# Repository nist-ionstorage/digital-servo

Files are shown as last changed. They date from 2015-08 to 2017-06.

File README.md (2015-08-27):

# NIST Digital Servo

Ion Storage Group  
Time and Frequency Division  
National Institute of Standards and Technology  
Boulder, CO USA

Authors:  
David Leibrandt (david.leibrandt@nist.gov)  
Jason Heidecker

The NIST digital servo is designed to be a general purpose feedback controller, implemented digitally using an FPGA.  The advantages of an all-digital approach include fast and easy (no soldering) reconfiguration of the feedback transfer function, loop shapes that go beyond PID, the ability to perform automatic lock acquisition, and the integration of diagnostics for easy analysis of open and closed loop system performance.  The NIST digital servo has been optimized for feedback control of lasers in atomic, molecular, and optical (AMO) physics experiments, but it should be applicable in other control applications with similar bandwidth, noise, and loop shape requirements.

This github repository contains the hardware, firmware, and software design files, as well as precompiled firmware and software binaries to run the digital servo on Windows 7.

For more information about the firmware and performance of the digital servo, as well as example use cases, please refer to D. R. Leibrandt and J. Heidecker, [arXiv:1508.06319](http://arxiv.org/abs/1508.06319) (2015).

For instructions on setting up the digital servo using the precompiled binaries on Windows 7 (which does not require installing or using any compilers) and on operation of the GUI, please see `doc\NIST_digital_servo_manual.pdf`.

The hardware design and fabrication files are located in the `hardware` folder.  The firmware source code files are located in the `firmware` folder.  The GUI source code files are located in the `gui` folder.  And matlab functions for reading in data files generated by the digital servo are located in the `matlab` folder.

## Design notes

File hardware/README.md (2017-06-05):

# OK6010_DB

Ion Storage Group  
Time and Frequency Division  
National Institute of Standards and Technology  
Boulder, CO USA

Authors:  
Jason Heidecker  
David Leibrandt (david.leibrandt@nist.gov)

The OK6010_DB is a an open source hardware daughterboard to the Opal Kelly XEM6010-LX150 that provides two channels of 100 MSPS 16 bit ADC, two channels of 100 MSPS 16 bit DAC, and one channel of 1 MSPS 20 bit DAC.

This directory contains all of the Altium Designer schematic and board files.  A complete set of fabrication files can be found in the `Project Outputs for OK6010_DB` folder.  Design files for an enclosure can be found in the `Enclosure` folder.

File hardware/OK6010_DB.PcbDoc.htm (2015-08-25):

Reporting Options

# File in Previous Format

Date | : | 8/14/2015
Time | : | 2:22:02 PM
Filename | : | C:\dev\digital-servo\hardware\OK6010_DB\OK6010_DB.PcbDoc

Version | Warning
Release 12 | CAUTION - Air Gap Width previously controlled by Clearance rule is now controlled by Polygon Connect Style rule's newly introduced Air Gap Width (set to default value). Suggest reviewing each Polygon Connect Style rule's Air Gap Width attribute for correctness.
Release 13 | CAUTION - Silkscreen Over Component Pads Rules are converted to Silk To Solder Mask Clearance Rules. Suggest examining rule scopes for accuracy.

This file was generated by an earlier version of the software

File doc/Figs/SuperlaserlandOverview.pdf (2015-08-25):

Fast
analog
input
settings settings

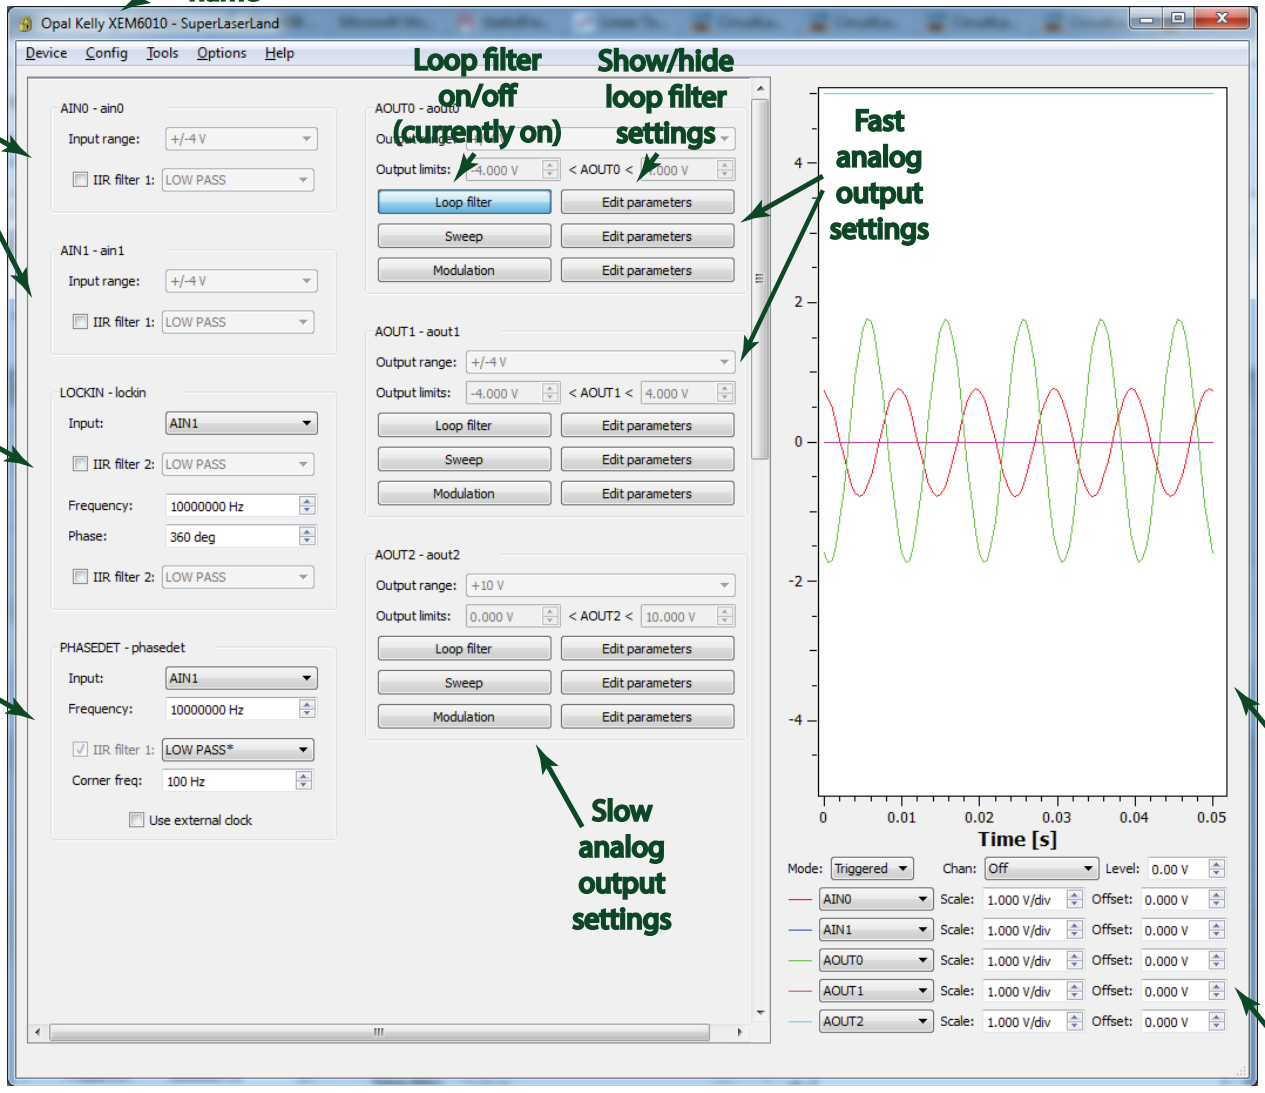
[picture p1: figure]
Fast analog output settings settings; Slow analog output settings settings; Loop filter Loop filter on/off (currently on) (currently on); Show/hide Show/hide loop filter loop filter settings settings

Lockin
amplifier amplifier
settings settings

Phase
detector detector
settings settings

Scope
settings settings

Scope
plot

Lock box Lock box
name

(b)

(a)

VGA setting VGA setting
Firmware output range limits Firmware output range limits

Loop filter input signal, offset, and sign Loop filter input signal, offset, and sign
Second order IIR filter (currently disabled) Second order IIR filter (currently disabled)

First order IIR filter First order IIR filter
(currently enabled and set to a PI loop shape) (currently enabled and set to a PI loop shape)

First order IIR filter First order IIR filter
(currently enabled and set to a PD loop shape) (currently enabled and set to a PD loop shape)

First order IIR filter (currently disabled) First order IIR filter (currently disabled)
Loop filter hold (currently disabled) Loop filter hold (currently disabled)
Loop filter hold falling and rising edge delay Loop filter hold falling and rising edge delay

Sweep center Sweep center
Sweep amplitude Sweep amplitude
Sweep frequency Sweep frequency

Amplitude of LOCKIN LO added to AOUT0 Amplitude of LOCKIN LO added to AOUT0

LOCKIN LO frequency LOCKIN LO frequency and phase and phase
LOCKIN post-filter LOCKIN post-filter

LOCKIN pre-filter LOCKIN pre-filter

LOCKIN input signal LOCKIN input signal

PHASEDET input signal PHASEDET input signal PHASEDET LO frequency PHASEDET LO frequency PHASEDET post-filter PHASEDET post-filter (currently set to a (currently set to a low-pass with a low-pass with a corner frequency corner frequency of 100 Hz.) of 100 Hz.)

AIN0 post-filter AIN0 post-filter (currently disabled) (currently disabled)

AOUT0 settings: AOUT0 settings: AIN0 VGA setting AIN0 VGA setting

Loop filter automatic relock (currently disabled) Loop filter automatic relock (currently disabled)

Loop filter clear when railed (currently disabled) Loop filter clear when railed (currently disabled)

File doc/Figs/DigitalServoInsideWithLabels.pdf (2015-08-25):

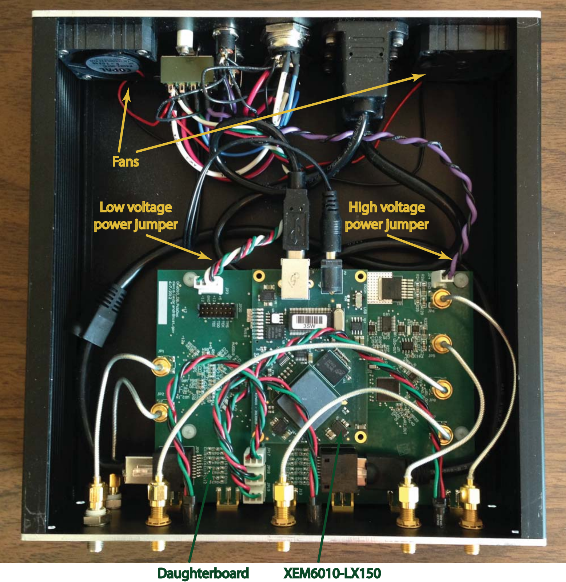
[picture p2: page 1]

Fans

Low voltage Low voltage
power jumper power jumper

High voltage High voltage
power jumper power jumper

Daughterboard Daughterboard XEM6010-LX150 XEM6010-LX150

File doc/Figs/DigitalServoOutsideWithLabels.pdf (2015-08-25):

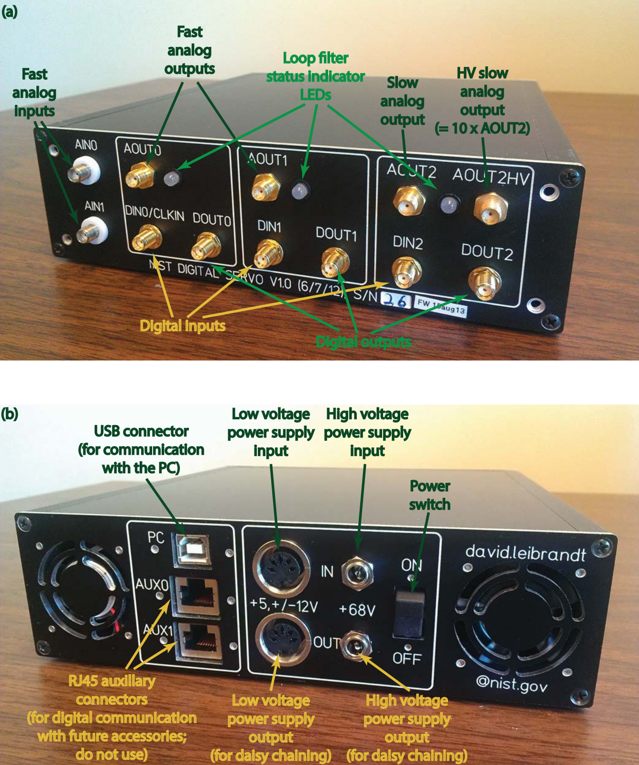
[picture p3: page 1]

Low voltage Low voltage
power supply power supply
input

High voltage High voltage
power supply power supply
input

Low voltage Low voltage
power supply power supply
output
(for daisy chaining) (for daisy chaining)

High voltage High voltage
power supply power supply
output
(for daisy chaining) (for daisy chaining)

Power
switch

USB connector USB connector (for communication (for communication with the PC) with the PC)

RJ45 auxillary RJ45 auxillary
connectors connectors
(for digital communication (for digital communication with future accessories; with future accessories; do not use) do not use)

(b)

(a)

Fast
analog
inputs

Fast
analog
outputs outputs
Slow
analog
output

HV slow HV slow
analog
output
(= 10 x AOUT2) (= 10 x AOUT2)

Digital inputs Digital inputs Digital outputs Digital outputs

Loop filter Loop filter
status indicator status indicator LEDs

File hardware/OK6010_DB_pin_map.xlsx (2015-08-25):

XEM6010 |  |  | FPGA |  |  |  | Daughterboard |  | Total |  | Differential | Mean |  | Notes
Jumper | Pin | Length [mm] | Bank | Description | Pin number | BUFIO2 Region | Description | Length [mm] | Length [mm] | Delay [ns] | Length [mm] | Delay [ns]
2 | 16 | 38.591 | 1 | L74P_1 | T19 | RB | AD5791_SCS |  |  |  |  |  |  | Each BUFIO2 region has
2 | 18 | 40.628 | 1 | L74N_1 | T20 | RB | AD5791_SCK |  |  |  |  |  |  |  | 4 BUFIO2s
2 | 20 | 39.602 | 1 | L72P_1 | P17 | RB | AD5791_SDI
2 | 22 | 33.852 | 1 | L72N_1 | N16 | RB | AD5791_SDO |  |  |  |  |  |  | Each bank has
2 | 28 | 36.711 | 1 | L73P_1 | P18 | RB | AD5791_LDAC |  |  |  |  |  |  |  | 2 BUFPLLs
2 | 26 | 34.914 | 1 | L71N_1 | M18 | RB | AD5791_CLR
2 | 24 | 34.813 | 1 | L71P_1 | M17 | RB | AD5791_RST |  |  |  |  |  |  | The XC6SLX45 has
 |  |  |  |  |  |  |  |  |  |  |  |  |  |  | 8 DCMs
1 | 17 | 35.889 | 1 | L9N_1 | G17 | RT | AD8251_IN_A0 |  |  |  |  |  |  |  | 4 PLLs
1 | 15 | 36.709 | 1 | L9P_1 | G16 | RT | AD8251_IN_A1 |  |  |  |  |  |  |  | 16 BUFGs
1 | 19 | 39.405 | 1 | L34P_1 | H19 | RT | AD8251_IN_WR0
1 | 21 | 36.649 | 1 | L34N_1 | H18 | RT | AD8251_IN_WR1 |  |  |  |  |  |  | Each IO tile can connect to
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

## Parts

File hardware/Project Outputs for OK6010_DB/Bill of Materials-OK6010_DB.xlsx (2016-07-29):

Designator | Comment | Footprint | Description | Quantity | Supplier 1 | Supplier Part Number 1 | Manufacturer 1 | Manufacturer Part Number 1
C1, C2, C9, C10, C40, C43 | 300pF | 0603w | capacitor | 6 | Digi-Key | 490-1438-1-ND | Murata Electronics North America | GRM1885C1H301JA01D
C3, C4, C8, C11, C14, C16, C17, C19, C22, C23, C28, C33, C34, C35, C39, C41, C42, C44, C45, C48, C50, C51, C54, C55, C58, C60, C62, C64, C65, C67, C68, C70, C72, C73, C76, C77, C78, C79, C80, C83, C85, C86, C87, C88, C89, C90, C91, C92, C94, C95, C96, C97, C99, C102, C103, C105, C106, C127 | 0.1uF | 0603w | capacitor | 58 | Digi-Key | 399-1281-1-ND | Kemet | C0603C104K3RACTU
C5, C7, C37, C38 | 0.1uF | 1206 | capacitor | 4 | Digi-Key | 490-1767-1-ND | Murata Electronics North America | GRM31C5C1E104JA01L
C6 | 2.2uF | 0805 CLL | INTERDIGITATED capacitor | 1 | Digi-Key | 445-3406-1-ND | TDK Corporation | CLLE1AX7S0G225M/0.95
C12 | 2.2uF | 0603w | capacitor | 1 | Digi-Key | 478-5316-1-ND | AVX Corporation | 06036C225KAT2A
C13, C15, C18, C20, C21, C30, C31, C32, C49, C52, C56, C59, C61, C63, C66, C69, C71, C74, C84, C98, C100, C104 | 10uF | 1206 | ELECTROLYTIC capacitor | 22 | Digi-Key | 493-4304-1-ND | Nichicon | F971C106MAA
C24, C29 | 33nF | 0805 | capacitor | 2 | Digi-Key | 490-3323-1-ND | Murata Electronics North America | GRM21BR72A333KA01L
C25 | 10pF | 0603w | capacitor | 1 | Digi-Key | 490-1403-1-ND | Murata Electronics North America | GRM1885C1H100JA01D
C26 | 10uF | 7243 V Type HD | ELECTROLYTIC capacitor | 1 | Digi-Key | PCE4986CT-ND | Panasonic Electronic Components | EEE-HD2A100P
C27 | 0.1uF | 0805 | capacitor | 1 | Digi-Key | 490-4789-1-ND | Murata Electronics North America | GCM21BR72A104KA37L
C36, C81, C82 | 1nF | 0603w | capacitor | 3 | Digi-Key | 490-1494-1-ND | Murata Electronics North America | GRM188R71H102KA01D
C46, C93 | 10uF | 0603w | capacitor | 2 | Digi-Key | 490-3896-1-ND | Murata Electronics North America | GRM188R60J106ME47D
C47, C53, C57, C75, C101 | 100uF | 1206 | capacitor | 5 | Digi-Key | 445-6008-1-ND | TDK Corporation | C3216X5R0J107M160AB
C107, C108, C109, C110 | 1.8pF | 0603w | capacitor | 4 | Digi-Key | 712-1328-1-ND | Johanson Technology Inc. | 251R14S1R8BV4T
C111, C112, C113, C114, C115, C116, C117, C118, C119, C120, C121, C122, C123, C124, C125, C126 | NOT STUFFED | 0603w | capacitor | 16
J11, J12, J13, J14, J15, J16 | SMA_EDGE | sma_edge | sma edge connector | 6 | Digi-Key | ACX1426-ND | Amphenol-RF Division | 132289
JP1, JP2, JP5, JP6, JP7, JP8 | SMA | sma_pcb_200 | sma connector | 6 | Digi-Key | A97594-ND | TE Connectivity AMP Connectors | 5-1814832-1
JP2_B, JP3_B | BTE-040-01-F-D-A | BTE-040-01-F-D-A | Samtec Connector 0.8mm 80pin | 2 | Newark | 89M7080 | SAMTEC | BTE-040-01-F-D-A
JP3 | SIP4 (PCB TERMINAL) | SIP4MOLEX | 4 pin molex connector | 1 | Digi-Key | WM2746-ND | Molex, LLC | 0022292041
JP4 | SIP2 (PCB TERMINAL) | SIP2MOLEX | 2 pin molex connector | 1 | Digi-Key | WM2744-ND | Molex, LLC | 0022292021
JP9, JP10 | RJ-45 | SMD_ETHERNET | ethernet connector | 2 | Digi-Key | RJSSE-5080-ND | Amphenol Commercial Products | RJSSE-5080
JP17, JP18, JP19 | SIP3 (PCB TERMINAL) | SIP3MOLEX | 3 pin molex connector | 3 | Digi-Key | WM2745-ND | Molex, LLC | 0022292031
JP20 | HEADER 7X2 | IDC14 SM 2MM | 14 pin 2mm IDC connector | 1 | Digi-Key | WM18641-ND | Molex, LLC | 0878321420
L1, L2, L7, L8, L9, L10, L11, L12, L15, L16, L25, L26, L27, L28 | 1.0uH | 1210 | inductor | 14 | Digi-Key | 490-2493-1-ND | Murata Electronics North America | LQH32CN1R0M23L
L3, L4, L5, L6, L13, L14, L17, L18, L19, L20, L21, L22, L23, L24 | 1.0uH | 0805 | inductor | 14 | Digi-Key | 490-4026-1-ND | Murata Electronics North America | LQM21FN1R0N00D
R1, R10, R11, R20 | 249* | 0603w | resistor | 4 | Digi-Key | RNCS0603BKE249RCT-ND | Stackpole Electronics Inc. | RNCS0603BKE249R
R2, R12 | 150* | 0603w | resistor | 2 | Digi-Key | RNCS0603BKE150RCT-ND | Stackpole Electronics Inc. | RNCS0603BKE150R
R3, R7, R13, R17 | 220* | 0603w | resistor | 4 | Digi-Key | RG16P220BCT-ND | Susumu | RG1608P-221-B-T5
R4, R6, R8, R14, R16, R18, R29, R30, R32, R33, R34, R36, R37, R38 | 49.9* | 0603w | resistor | 14 | Digi-Key | RNCS0603BKE49R9CT-ND | Stackpole Electronics Inc. | RNCS0603BKE49R9
R5, R15 | 100k | 0603w | resistor | 2 | Digi-Key | 311-100KHRCT-ND | Yageo | RC0603FR-07100KL
R9, R19 | 1M | 0603w | resistor | 2 | Digi-Key | 311-1.00MHRCT-ND | Yageo | RC0603FR-071ML
R21 | 1.5k | 0603w | resistor | 1 | Digi-Key | 311-1.50KHRCT-ND | Yageo | RC0603FR-071K5L
R22, R41 | 140k | 0603w | resistor | 2 | Digi-Key | 311-140KHRCT-ND | Yageo | RC0603FR-07140KL
R23, R26 | 49.9* | 1206 | resistor | 2 | Digi-Key | RG32P49.9BCT-ND | Susumu | RG3216P-49R9-B-T1
R24 | 9.1k * | 0805 | resistor | 1 | Digi-Key | RG20P9.1KBCT-ND | Susumu | RG2012P-912-B-T5
R25 | 1k * | 0805 | resistor | 1 | Digi-Key | RG20P1.0KBCT-ND | Susumu | RG2012P-102-B-T5
R27 | 1K | 0603w | resistor | 1 | Digi-Key | 311-1.00KHRCT-ND | Yageo | RC0603FR-071KL
R28 | 287 | 0603w | resistor | 1 | Digi-Key | 311-287HRCT-ND | Yageo | RC0603FR-07287RL
R31 | 10k* | 0603w | resistor | 1 | Digi-Key | RG16P10.0KBCT-ND | Susumu | RG1608P-103-B-T5
R35, R39, R62, R63, R64, R65, R66, R67, R68, R69 | 0 | 0603w | resistor | 10 | Digi-Key | P0.0GCT-ND | Panasonic Electronic Components | ERJ-3GEY0R00V
R40, R42 | 78.7k | 0603w | resistor | 2 | Digi-Key | 311-78.7KHRCT-ND | Yageo | RC0603FR-0778K7L
R43, R45 | 76.8k | 0603w | resistor | 2 | Digi-Key | 311-76.8KHRCT-ND | Yageo | RC0603FR-0776K8L
R44, R46 | 147k | 0603w | resistor | 2 | Digi-Key | 311-147KHRCT-ND | Yageo | RC0603FR-07147KL
R47 | 10k | VFCD1505 | resistor network | 1 | Digi-Key | Y1685-10K/10K-ND | Vishay Foil Resistors (Division of Vishay Precision Group) | Y1685V0001TT9W
R48 | 107k | 0603w | resistor | 1 | Digi-Key | 311-107KHRCT-ND | Yageo | RC0603FR-07107KL
R49 | 93.1K | 0603w | resistor | 1 | Digi-Key | 311-93.1KHRCT-ND | Yageo | RC0603FR-0793K1L
R50, R51, R52, R53 | 2k | 0603w | resistor | 4 | Digi-Key | 311-2.00KHRCT-ND | Yageo | RC0603FR-072KL
R54, R55, R56, R57 | 75* | 0603w | resistor | 4 | Digi-Key | RNCS0603BKE75R0CT-ND | Stackpole Electronics Inc. | RNCS0603BKE75R0
R58, R59, R60, R61, R70, R71 | 62 | 0603w | resistor | 6 | Digi-Key | 541-62.0HCT-ND | Vishay Dale | CRCW060362R0FKEA
U1 | LTC2195 | UKG - QFN52 | 16 bit, low power, dual ADC | 1 | Digi-Key | LTC2195CUKG#PBF-ND | Linear Technology | LTC2195CUKG#PBF
U2, U4, U13, U14 | AD8251 | MSOP10sm | Programmable Gain Instumentation Amp, IC AMP INST ICMOS LDRIFT 10MSOP, IC AMP INST ICMOS LDRIFT 10MSOP, IC AMP INST ICMOS LDRIFT 10MSOP | 4 | Digi-Key | AD8251ARMZ-ND | Analog Devices Inc. | AD8251ARMZ
U3, U5 | LTC6406 | MSOP08 | Differential ADC Driver | 2 | Digi-Key | LTC6406CMS8E#PBF-ND | Linear Technology | LTC6406CMS8E#PBF
U6 | ADR127 | TSOT-6 | Voltage Reference | 1 | Digi-Key | ADR127AUJZ-REEL7CT-ND | Analog Devices Inc. | ADR127AUJZ-REEL7
U7 | ADR445B | SOIC08 | Ultra Precision Low Noise XFET Voltage Reference | 1 | Digi-Key | ADR445BRZ-ND | Analog Devices Inc. | ADR445BRZ
U8 | AD8676 | MSOP08 | ultraprecision dual rail-to-rail op amp | 1 | Digi-Key | AD8676BRMZ-REELCT-ND | Analog Devices Inc. | AD8676BRMZ-REEL
U9, U19 | AD8675 | MSOP08 | ultraprecision rail-to-rail op amp | 2 | Digi-Key | AD8675ARMZ-REELCT-ND | Analog Devices Inc. | AD8675ARMZ-REEL
U10 | AD5791 | TSSOP20 | DAC 20BIT SRL 20TSSOP | 1 | Digi-Key | AD5791ARUZ-ND | Analog Devices Inc. | AD5791ARUZ
U11 | OPA453 | DDPAK-7 | 80 V op amp | 1 | Mouser | 595-OPA453FAKTWT | Loading... | Loading...
U12 | AD9783 | LFCSP72 | DAC LVDS DUAL16BIT 500MSPS | 1 | Digi-Key | AD9783BCPZ-ND | Analog Devices Inc. | AD9783BCPZ
U15, U16, U17, U18, U20 | ADP3336 | MSOP08 | regulator | 5 | Digi-Key | ADP3336ARMZ-REEL7CT-ND | Analog Devices Inc. | ADP3336ARMZ-REEL7

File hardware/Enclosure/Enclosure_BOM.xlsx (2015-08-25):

Description | Quantity | Supplier | Supplier part #
Power supply +5V, +/-12V | 1 | Newark | 28M9050
Bulkhead 5 pin DIN | 2 | Digikey | CP-1235-ND
Power jumper cable, 1 ft | 0 | Amazon | http://www.amazon.com/Hosa-MID301BK-Standard-Cable-Black/dp/B000068NTK/ref=zg_bs_11973431_11
Power supply connector | 0 | Newark | SP119M-5P
56 V power supply | 1 | Digikey | 993-1023-ND
Bulkhead 2.1mm jack | 2 | Digikey | CP-5-ND
HV power jumper cable, 1 ft | 0 | Amazon | http://www.amazon.com/Male-2-1mm-Plug-Power-Adapter/dp/B0048O2XXG/ref=pd_sim_sbs_p_7
4PDT rocker switch | 1 | Digikey | 360-2276-ND
0.25" 2-56 standoff | 2 | Digikey | 492-1059-ND
2-56 x 3/8" socket cap screw | 2 | Mcmaster | 92196A079
Ethernet bulkhead female to male | 2 | Frontx | P115, 12 inch
USB bulkhead female to male | 1 | Frontx | P112, 6 inch
4-40 x 1/4" socket cap screw | 6 | Mcmaster | 92196A106
Fan | 2 | Digikey | 563-1130-ND
4-40 x 3/8" socket cap screw | 8 | Mcmaster | 92196A108
Bulkhead SMA female to SMA female, isolated ground | 2 | Pasternack | PE9067
Bulkhead SMA female to SMA female | 4 | Digikey | ARF1207-ND
Two color LED | 3 | Digikey | 350-2131-ND
0.438" 4-40 plastic standoff | 4 | Digikey | 492-1092-ND
4-40 plastic washer | 4 | Digikey | 3348K-ND
0.625" 4-40 plastic screw | 4 | Digikey | H548-ND
XEM6010 power connector | 1 | Digikey | CP-2185-ND
Enclosure front panel | 1 | Front panel express | front.fpd
Enclosure back panel | 1 | Front panel express | back.fpd
Enclosure top panel | 1 | Front panel express | top.fpd
Enclosure bottom panel | 1 | Front panel express | bottom.fpd
Enclosure side panel | 2 | Front panel express | GL GP 10 23 - 200
Enclosure assembly kit (screws and feet) | 1 | Front panel express | GG MS 1123
Rack mount panel | 0.5 | Front panel express | rack mount panel.fpd
2 pin molex connector | 1 | Digikey | WM2613-ND
3 pin molex connector | 3 | Digikey | WM2626-ND
4 pin molex connector | 1 | Digikey | WM2614-ND
Molex connector terminals | 15 | Digikey | WM2624-ND
4" SMA cable | 3 | Digikey | ACX1664-ND
5" SMA cable | 2 | Digikey | ACX1665-ND
7" SMA cable | 1 | Digikey | ACX1667-ND
FPGA heat sink | 1 | Newark | 46T6813
FPGA integration PCB | 1 | Opal Kelly | XEM6010-LX150
Custom daughterboard PCB | 1 | Any | OK6010_DB

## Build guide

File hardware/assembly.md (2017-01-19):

Assembly instructions for the digital-servo box. 

## enclosure continutity
For safety reasons all sides of enclosure must be shorted to GND on power supply cable. 

## grounding of enclosure electrical connectors
All connector shields are shorted to enclosure except JP1 and JP2 which use isolated SMA.

## LED wiring
JP18, JP18, JP19 are labeled with GRN, GND, RED which corresponds to
the wire colors of the specified LEDs.

## AUX connector wiring 
AUX0 and AUX1 are used for expansion options. 
- AUX0 is routed to JP9. 
- AUX1 is routed to JP10.

## power connectors
Refer to the photo [here](https://github.com/nist-ionstorage/digital-servo/blob/master/doc/Figs/DigitalServoOutsideWithLabels.pdf). 

- For "Low voltage power supply input" and "Low voltage power supply
output" match wiring on connector from power supply brick 
(AEH45UM31 or [PCM50UT04](http://datasheet.octopart.com/PCM50UT04-XP-Power-datasheet-3173.pdf)).

- +5, -12, +12, GNDs from "Low voltage power supply input" are
permanently shorted to +5, -12, +12, GNDs on "Low voltage power supply
output".

- +68V on "High goltage power supply input" is permanently shorted to
"High voltage power supply output".

## power switch
Power Switch connects/disconnects -12, +12, +5, +68 to JP3, JP4 and the fans.

## wire color choice
If practical duplicate the wire color choice as in 
[this](https://github.com/nist-ionstorage/digital-servo/blob/master/doc/Figs/DigitalServoInsideWithLabels.pdf) photo. 

## wire gauge
Current for all power supplies is <= 5.0 A. Based on [this]
(http://assets.bluesea.com/files/resources/newsletter/images/DC_wire_selection_chartlg.jpg)
chart <= 16 AWG is sufficient. Use multi-strand wires throughout the
design (no mono-filament).

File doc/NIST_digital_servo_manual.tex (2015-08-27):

\documentclass[aip,rsi,preprint,graphicx]{revtex4-1}
\usepackage{graphicx}  % needed for figures
\usepackage{dcolumn}   % needed for some tables
\usepackage{bm}           % for math
\usepackage{amssymb} % for math
\usepackage{amsmath} % for math
\usepackage{hyperref} % for links

% avoids incorrect hyphenation
\hyphenation{FPGAs}

\begin{document}

\title{NIST digital servo manual}

\author{David~R.~Leibrandt}
\email{david.leibrandt@nist.gov}
\affiliation{National Institute of Standards and Technology\\325 Broadway St.~Boulder, CO 80305\\USA}

\date{\today}

\maketitle

\tableofcontents

%%%%%%%%%%%%%%%%%%%%%%%%%%%%%%%%%%%%%%%%%%%%%%%%%%
\section{Introduction}
%%%%%%%%%%%%%%%%%%%%%%%%%%%%%%%%%%%%%%%%%%%%%%%%%%

The NIST digital servo is designed to be a general purpose feedback controller, implemented digitally using an FPGA.  The advantages of an all-digital approach include fast and easy (no soldering) reconfiguration of the feedback transfer function, loop shapes that go beyond PID, the ability to perform automatic lock acquisition, and the integration of diagnostics for easy analysis of open and closed loop system performance.  The NIST digital servo has been optimized for feedback control of lasers in atomic, molecular, and optical (AMO) physics experiments, but it should be applicable in other control applications with similar bandwidth, noise, and loop shape requirements.  The key specifications (of hardware V1.0) are are:
\begin{itemize}
\item 1 FPGA (Xilinx Spartan 6 LX150)
\item 2 fast analog input channels (LTC2195, 16 bit, 100 MSPS, 50~nV$/\sqrt{\textrm{Hz}}$)
\item 2 fast analog output channels (AD9783, 16 bit, 100 MSPS, 40~nV$/\sqrt{\textrm{Hz}}$)
\item 1 slow analog output channel (AD5791, 20 bit, 1 MSPS, 20~nV$/\sqrt{\textrm{Hz}}$, optionally amplified to 0V to +65V output range for direct drive of PZTs)
\item Several digital I/O channels
\item 320 ns analog latency (ADC, digital signal processing, and DAC) including a digital PI filter
\item USB communication and GUI for setup and diagnostics
\end{itemize}

This manual describes assembly, setup, and operation of the NIST digital servo.  Section~\ref{sec:quickStart} describes how to assemble the hardware, load the firmware, and install the GUI.  Section~\ref{sec:software} describes how to use the GUI.  For more information about the firmware and performance of the digital servo, as well as example use cases, please read D.~R.~Leibrandt and J.~Heidecker, \href{http://arxiv.org/abs/1508.06319}{arXiv:1508.06319} (2015).

%%%%%%%%%%%%%%%%%%%%%%%%%%%%%%%%%%%%%%%%%%%%%%%%%%
\section{Quick start guide}\label{sec:quickStart}
%%%%%%%%%%%%%%%%%%%%%%%%%%%%%%%%%%%%%%%%%%%%%%%%%%

In order to get started, you will need need:
\begin{itemize}
\item A set of parts to assemble the digital servo hardware box (see \\{\tt digital-servo\textbackslash hardware\textbackslash Enclosure\textbackslash Enclosure\_BOM.xlsx})
\item A low voltage power supply (+5~V, $\pm$12~V; the hardware has been tested successfully with ASTEC model DPT52)
\item A high voltage power supply (up to +68~V; the hardware has been tested successfully with PHIHONG USA model PSAC30U-560)
\item A USB cable
\item A computer (this manual will assume use of the Windows 7 operating system, but we have also compiled and run the digital servo using Linux)
\item Copies of the following software
\begin{itemize}
\item The digital servo GUI and the Qt, Qwt, and Opal Kelly libraries
\item The Opal Kelly USB communication driver
\end{itemize}
\end{itemize}

\subsection{Hardware assembly}

The hardware consists of an Opal Kelly XEM6010-LX150 FPGA evaluation board and a custom daughterboard, packaged together with some fans, some LEDs, and a switch in an enclosure.  Here we assume that the daughterboard has already been fabricated and stuffed, which can be done by a PCB assembly company.  To assemble the digital servo hardware, follow these steps:

\begin{enumerate}
\item Install the connectors, LEDs, fans, and switch onto enclosure front and back panels and wire them up, following Fig.~\ref{fig:DigitalServoInsidePic}
\item Double check that one of the fans blows air into the box and the other blows air out of the box
\item Remove FB2 from the XEM6010-LX150
\item Add the heat sink to the FPGA
\item Press XEM6010-LX150 and the daughterboard together
\item Attach the daughterboard to the enclosure bottom using nylon washers on top so that the screws do not stick out bottom of the box
\item Put the enclosure together and connect the wires
\end{enumerate}

\begin{figure*}
\begin{center}

\caption{\label{fig:DigitalServoInsidePic}Picture of the inside of an assembled NIST digital servo box.}
\end{center}
\end{figure*}

When assembly is complete, the hardware box should look like that shown in Fig.~\ref{fig:DigitalServoOutsidePic}.

\begin{figure*}
\begin{center}

\caption{\label{fig:DigitalServoOutsidePic}Pictures of the (a) front and (b) back of a NIST digital servo box.  Inputs and outputs are labeled.}
\end{center}
\end{figure*}

\subsection{Loading the firmware}\label{sec:loadFirmware}

The firmware is stored in a FLASH memory on the XEM6010-LX150 and loaded automatically upon turning on the power, so these steps will only need to be executed once after the box is built to load the firmware into the FLASH.  To load the firmware, you will need to use the program flashloader.exe, which ships with the XEM6010-LX150.  Follow these steps:

\begin{enumerate}
\item Install the Opal Kelly communication driver on your computer by running the executable {\tt Setup-Win-Win32-4.0.8.exe} (located in the folder {\tt Opal\_Kelly\_2012\_02\_07} on the Opal Kelly CD) and follow the instructions.
\item Copy flashloader.exe (located in the \\{\tt C:\textbackslash Program~Files\textbackslash Opal~Kelly\textbackslash FrontPanelUSB\textbackslash Samples\textbackslash FlashLoader} folder) and flashloader.bit (located on the Opal Kelly CD in the \\{\tt Opal\_Kelly\_2012\_02\_07\textbackslash Bitfiles\textbackslash 20111007-FP40-XEM6010-LX150.zip\textbackslash XEM6010-LX150} folder) to the \\{\tt digital-servo\textbackslash deploy\textbackslash Windows7\_FW28may15} folder.  
\item Unplug all other digital servo boxes from the computer so that flashloader.exe will select the correct box for for programming.
\item Plug in the digital servo power and USB connections and flip the dip switch on the XEM6010-LX150 to ``USB'' (you will have to open the digital servo enclosure), then flip the power switch to the on position.
\item Open a command prompt (search for ``cmd'' in the Start Menu) and navigate to the \\{\tt digital-servo\textbackslash deploy\textbackslash Windows7\_FW28may15} folder.
\item Execute \\{\tt flashloader.exe superlaserland\_HW07jun12\_CONFIG\_SIMPLEPI\_FW28may15.bit}
\item Flip the dip switch on the XEM6010-LX150 to ``PROM'', then power cycle the digital servo and close up the enclosure.
\end{enumerate}

\subsection{Installing the software}\label{sec:installSoftware}

Follow these steps to install the GUI:

\begin{enumerate}
\item If you have not already done so on this computer, install the Opal Kelly communication driver (see Section~\ref{sec:loadFirmware}, step 1).
\item Copy okFrontPanel.dll (located in the \\{\tt C:\textbackslash Program~Files\textbackslash Opal~Kelly\textbackslash FrontPanelUSB\textbackslash API-32} folder) to the \\{\tt digital-servo\textbackslash deploy\textbackslash Windows7\_FW28may15} folder.
\item Create an empty folder {\tt C:\textbackslash data\textbackslash SuperLaserLand}.  This is the location where any data saved by the digital servo can be found.
\item Connect the low voltage and high voltage power supplies.  Note that there are two connectors for each power supply on the back of the digital servo box.  This is to allow running up to four digital servo boxes on a single pair of power supplies, using daisy chain cables.  Also note that if you do not intend to use the high voltage output (AOUT2HV), you do not need the high voltage power supply.
\item Ensure that the power switch on the back of the digital servo is in the off position, then connect the USB cable to the back of the digital servo box and to your PC.
\item Flip the power switch on the back of the digital servo to the on position and wait 15~s for the FPGA to initialize.
\item Run the executable {\tt SuperLaserLand\_FW28may15.exe} and you should be ready to go!  See Sec.~\ref{sec:software} for a description of how to use the GUI.
\end{enumerate}

%%%%%%%%%%%%%%%%%%%%%%%%%%%%%%%%%%%%%%%%%%%%%%%%%%
\section{Graphical user interface}\label{sec:software}
%%%%%%%%%%%%%%%%%%%%%%%%%%%%%%%%%%%%%%%%%%%%%%%%%%

Communication between the NIST digital servo hardware and the computer is facilitated by a GUI program called SuperLaserLand (see Fig.~\ref{fig:SoftwareScreenshot}).  Follow the instructions found in Sec.~\ref{sec:installSoftware} in order to launch SuperLaserLand.

\begin{figure*}
\begin{center}

\caption{\label{fig:SoftwareScreenshot}Screen shots of the SuperLaserLand GUI.  The settings for the AOUT loop filter, sweep, and modulation can be (a) hidden or (b) shown.  Most of the configuration settings are labeled.}
\end{center}
\end{figure*}

\subsection{{\tt Device} menu}

The {\tt Device} menu contains commands pertaining to the digital servo hardware.  The {\tt Set name} command is used to set the name of the digital servo box.  This name is displayed at the top left of the SuperLaserLand window and is helpful when communicating with multiple digital servo boxes using a single PC.  If the GUI is launched when more than one digital servo box is connected to the computer, the user will be asked to select the hardware box they wish to communicate with by this name.  The {\tt Send command}, {\tt Optimize LTC2195 timing}, and {\tt Optimize AD9783 timing} commands are used for debugging and should not be needed by the typical user.

\subsection{{\tt Config} menu}

The {\tt Config} menu contains commands for saving and loading the digital servo configuration (i.e., digital signal processing settings).  The current configuration can be saved to or loaded from a FLASH memory located in the digital servo box using the {\tt Save to FLASH} or {\tt Load from FLASH} commands.  The FLASH memory can only hold one configuration at a time, so any previously saved configuration is overwritten each time the {\tt Save to FLASH} command is used.  The FLASH memory is nonvolatile, and the configuration saved in the FLASH memory is loaded automatically on power up.  The current configuration can also be saved to or loaded from the PC, using the {\tt Save to file} or {\tt Load from file} commands.  This allows the user to save multiple configuration files and to transfer the configuration from one digital servo to another (via the PC).

\subsection{{\tt Tools} menu}

The {\tt Tools} menu contains commands used for diagnostics of the digital servo and the system under servo control.

The {\tt Record data} command is used to record all of the digital servo signals to a binary file on the PC at a user defined sample rate and for a user defined total number of samples.  The resulting data file can be found in {\tt C:\textbackslash data\textbackslash SuperLaserLand} and is labeled {\tt <TIMESTAMP>.dat}.  It can be read into matlab using the function \\{\tt readSuperLaserLandSimplePI.m} located in the {\tt digital-servo\textbackslash matlab} folder.

The {\tt Measure transfer function} command is used to measure transfer functions.  It temporarily adds a swept sinusoidal modulation to one of the analog outputs.  For each value of the modulation frequency, a data file containing the values of digital servo signals is recorded to the PC (by internally calling the {\tt Record data} command).  The data files can be found in the directory {\tt C:\textbackslash data\textbackslash SuperLaserLand\textbackslash <TIMESTAMP>} and are labeled {\tt <MODULATION FREQ>.dat}.  Data processing to compute the transfer function from the recorded files is performed offline in matlab.

\subsection{{\tt Options} menu}

The {\tt Options} menu contains software options.

The {\tt Edit analog configuration} option must be enabled in order to be able to change the analog input and output ranges.  This prevents the user from accidentally changing the input and output ranges, which in some circumstances may damage the system under servo control.  In addition, when the {\tt Edit analog configuration} option is enabled, the user can change the names of the analog signals by typing a new name in the {\tt Name} text field that appears at the top of the signal box {\it and pressing enter}.  For instance, AIN0 could be renamed ``HC error signal'' and AOUT2 could be named ``PZT''.  These names are saved with the digital servo configuration.

When the {\tt Log data} option is enabled, the digital servo records the values of the analog signals to a text file on the PC at a user defined interval, indefinitely.  At the end of each time interval the minimum, maximum, and mean values of each signal over the time interval are recorded.  The data file can be found in {\tt C:\textbackslash data\textbackslash SuperLaserLand} and is labeled {\tt <TIMESTAMP>.csv}.  It can be read into matlab using the function {\tt readSLLlog.m} located in the {\tt digital-servo\textbackslash matlab} folder.

\subsection{Analog input configuration}

Each analog input has configuration settings located in the {\tt AIN0} and {\tt AIN1} boxes that allow processing of the input signals before they are used for feedback.  The gain of the VGA before the ADC can be set using the {\tt Input range} drop down list, which can only be accessed when the {\tt Edit analog configuration} option is enabled.  In addition, the digitized ADC signal can optionally be filtered by a first order IIR filter.  In order to enable the IIR filter, click the checkbox to the left of the label {\tt IIR filter 1} (which stands for first order IIR filter).  The filter shape can be changed using the drop down list, and the filter parameters can be set using the numerical input boxes below.  For example, when the filter shape is set to {\tt LOW PASS}, the low-pass corner frequency and gain can be adjusted.

\subsection{Lock-in amplifier configuration}

The lock-in amplifier settings are located in the box labeled {\tt LOCKIN}.  From top to bottom the settings are the input signal ({\tt Input} drop down list), the second order IIR pre-filter (top {\tt IIR filter 2}), the LO frequency and demodulation phase, and the second order IIR post-filter (bottom {\tt IIR filter 2}).

\subsection{Phase detector configuration}

The phase detector settings are located in the box labeled {\tt PHASEDET}.  From top to bottom the settings are the input signal ({\tt Input} drop down list), the LO frequency, the first order low-pass IIR filter frequency, and the use external clock setting.  Note that that majority of the FPGA is clocked on an internal crystal oscillator clock, and that the phase detector optionally uses an external clock to clock the local oscillator.  The external clock must be a square wave fed into DIN0, have a low level of 0~V and a high level of 3.3~V, and have a frequency of 10~MHz.

\subsection{Analog output configuration}

The analog output settings are located in the {\tt AOUT0}, {\tt AOUT1}, and {\tt AOUT2} boxes.  The gain of the VGA after the DAC can be set using the {\tt Output range} drop down list and the firmware output range limits can be set using the {\tt Output limits} numerical input boxes.  These settings can only be accessed when the {\tt Edit analog configuration} option is enabled.

Each analog output signal is generated as the sum of a loop filter, a sweep module that generates a triangle wave sweep, and a relock module that performs automatic lock acquisition.

The analog output loop filter can be turned on or off using the {\tt Loop filter} button.  When SuperLaserLand is first opened, the loop filter settings are hidden.  In order to display the loop filter settings, press the {\tt Edit parameters} button to the right of the {\tt Loop filter} button.  The loop filter input can be set to any of the analog signals with an optional constant offset and sign flip.  The loop filter consists of one or more first and second order IIR filters applied sequentially to the input signal.  The settings for these filters are shown from top to bottom in the order the filters are applied, starting with a second order IIR filter ({\tt IIR filter 2}) and followed by one to three first order IIR filters ({\tt IIR filter 1}).  Only the first first-order IIR filter must be enabled; the other IIR filters are optional.  For example, a ``PIID'' loop shape can be configured by disabling the second order IIR filter and enabling the three first order IIR filters, with loop shapes PI, PI, and PD.  Alternatively, an integrator with a notch (appropriate for feedback to a PZT with a resonance) can be configured by enabling the second order IIR filter and the first first-order IIR filter with loop shapes I/HO and P (note that I/HO stands for integrator divided by harmonic oscillator).  Note that the first and second order IIR filters have latencies of 30 and 80 ns.  The latency of each module should be kept in mind when selecting a loop filter configuration for high-bandwidth applications.

An optional loop filter hold feature (``integrator hold'') can be enabled using the checkbox to the left of the label {\tt Hold}.  When this feature is enabled, the output of the loop filter will be constant when the signal selected to the right of the label {\tt Hold} is boolean true.  When DIN0, DIN1, or DIN2 is selected, the loop filter output is held constant when the digital input is TTL high.  When !DIN0, !DIN1, or !DIN2 is selected, the loop filter output is held constant when the digital input is TTL low.  When LOOP FILTER 0, 1, or 2 is selected, the loop filter output is held constant when the other loop filter is unlocked (which is detected only if the relock feature on that loop filter is enabled).  The falling and rising edges of the hold signal can optionally be delayed by independent time intervals, which are set using the {\tt Falling delay} and {\tt Rising delay} input boxes.  This feature is useful, for instance, when performing intensity stabilization of a short laser pulse.

An optional loop filter automatic relock feature can be enabled using the checkbox to the left of the label {\tt Relock}.  To the right of the {\tt Relock} label there is a drop down list that allows the user to select the signal that will determine whether the loop filter is locked or not.  When an analog signal is selected, the loop filter is considered locked when the value of that analog signal is between the user input bounds.  When a digital signal is selected, the loop filter is considered locked when the digital signal is TTL low.  When the loop filter is unlocked, the relock feature sweeps the output of the loop filter in a triangle wave with an amplitude that increases with time and a (constant) user selected slew rate, until lock is reacquired.

Finally, the loop filter output can optionally be reset to zero when it reaches one of the output limits using the checkbox to the left of the label {\tt Clear integrators when railed}.  This feature is useful for locking cavities or interferometers where the error signal is periodic and it does not matter to which fringe the system is locked.

The analog output sweep can be turned on or off using the {\tt Sweep} button, and the sweep settings can be shown by pressing the {\tt Edit parameters} button to the right of the {\tt Sweep} button.  The sweep is a triangle wave, with adjustable offset ({\tt Center} input box), amplitude, and frequency.  In order to DC bias the analog output, turn on the sweep with zero amplitude.

The lock-in amplifier LO can be added to the analog output by pressing the {\tt Modulation} button, and the modulation amplitude can be shown and adjusted by pressing the {\tt Edit parameters} button to the right of the {\tt Modulation} button.

\subsection{Scope configuration}

The right side of the SuperLaserLand GUI contains a basic oscilloscope that can be used to display the digital servo signals in real-time.  The oscilloscope has three modes: Off, Rolling, and Triggered.  When Rolling mode is selected the time base of the scope is 20~s, and when Triggered mode is selected the time base of the scope is 50~ms.  These are not adjustable.  The oscilloscope can display up to five traces simultaneously.  For each trace, the user can select the digital servo signal to be displayed, the vertical scale, and the vertical offset.

\end{document}
%
% ****** End of file template.aps ******

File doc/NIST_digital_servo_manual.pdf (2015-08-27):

NIST digital servo manual

David R. Leibrandt¹, a)

National Institute of Standards and Technology

325 Broadway St. Boulder, CO 80305

USA

(Dated: 27 August 2015)

a)Electronic mail: david.leibrandt@nist.gov

CONTENTS

I. Introduction | 2
II. Quick start guide | 3
A. Hardware assembly | 4
B. Loading the firmware | 4
C. Installing the software | 7
III. Graphical user interface | 8
A. Device menu | 8
B. Config menu | 8
C. Tools menu | 10
D. Options menu | 10
E. Analog input configuration | 11
F. Lock-in amplifier configuration | 11
G. Phase detector configuration | 11
H. Analog output configuration | 12
I. Scope configuration | 14
I. INTRODUCTION

The NIST digital servo is designed to be a general purpose feedback controller, imple-

mented digitally using an FPGA. The advantages of an all-digital approach include fast

and easy (no soldering) reconfiguration of the feedback transfer function, loop shapes that

go beyond PID, the ability to perform automatic lock acquisition, and the integration of

diagnostics for easy analysis of open and closed loop system performance. The NIST digital

servo has been optimized for feedback control of lasers in atomic, molecular, and optical

(AMO) physics experiments, but it should be applicable in other control applications with

similar bandwidth, noise, and loop shape requirements. The key specifications (of hardware

V1.0) are are:

- 1 FPGA (Xilinx Spartan 6 LX150)
- 2 fast analog input channels (LTC2195, 16 bit, 100 MSPS, 50 nV/

√
Hz)

- 2 fast analog output channels (AD9783, 16 bit, 100 MSPS, 40 nV/

√
Hz)
- 1 slow analog output channel (AD5791, 20 bit, 1 MSPS, 20 nV/

√
Hz, optionally am-

plified to 0V to +65V output range for direct drive of PZTs)

- Several digital I/O channels
- 320 ns analog latency (ADC, digital signal processing, and DAC) including a digital

PI filter

- USB communication and GUI for setup and diagnostics

This manual describes assembly, setup, and operation of the NIST digital servo. Section II

describes how to assemble the hardware, load the firmware, and install the GUI. Section III

describes how to use the GUI. For more information about the firmware and performance of

the digital servo, as well as example use cases, please read D. R. Leibrandt and J. Heidecker,

arXiv:1508.06319 (http://arxiv.org/abs/1508.06319) (2015).

II. | QUICK START GUIDE
| In order to get started, you will need need:
| • A set of parts to assemble the digital servo hardware box (see
| digital-servo\hardware\Enclosure\Enclosure BOM.xlsx)
| • A low voltage power supply (+5 V, ±12 V; the hardware has been tested successfully
| with ASTEC model DPT52)
| • A high voltage power supply (up to +68 V; the hardware has been tested successfully
| with PHIHONG USA model PSAC30U-560)
| • A USB cable
| • A computer (this manual will assume use of the Windows 7 operating system, but we
| have also compiled and run the digital servo using Linux)
| • Copies of the following software
| – The digital servo GUI and the Qt, Qwt, and Opal Kelly libraries
| – The Opal Kelly USB communication driver

A. Hardware assembly

The hardware consists of an Opal Kelly XEM6010-LX150 FPGA evaluation board and a

custom daughterboard, packaged together with some fans, some LEDs, and a switch in an

enclosure. Here we assume that the daughterboard has already been fabricated and stuffed,

which can be done by a PCB assembly company. To assemble the digital servo hardware,

follow these steps:

1. Install the connectors, LEDs, fans, and switch onto enclosure front and back panels

and wire them up, following Fig. 1

2. Double check that one of the fans blows air into the box and the other blows air out

of the box

3. Remove FB2 from the XEM6010-LX150
4. Add the heat sink to the FPGA
5. Press XEM6010-LX150 and the daughterboard together
6. Attach the daughterboard to the enclosure bottom using nylon washers on top so that

the screws do not stick out bottom of the box

7. Put the enclosure together and connect the wires

When assembly is complete, the hardware box should look like that shown in Fig. 2.

B. Loading the firmware

The firmware is stored in a FLASH memory on the XEM6010-LX150 and loaded auto-

matically upon turning on the power, so these steps will only need to be executed once after

the box is built to load the firmware into the FLASH. To load the firmware, you will need to

use the program flashloader.exe, which ships with the XEM6010-LX150. Follow these steps:

1. Install the Opal Kelly communication driver on your computer by running the exe-

cutable Setup-Win-Win32-4.0.8.exe (located in the folder Opal Kelly 2012 02 07

on the Opal Kelly CD) and follow the instructions.

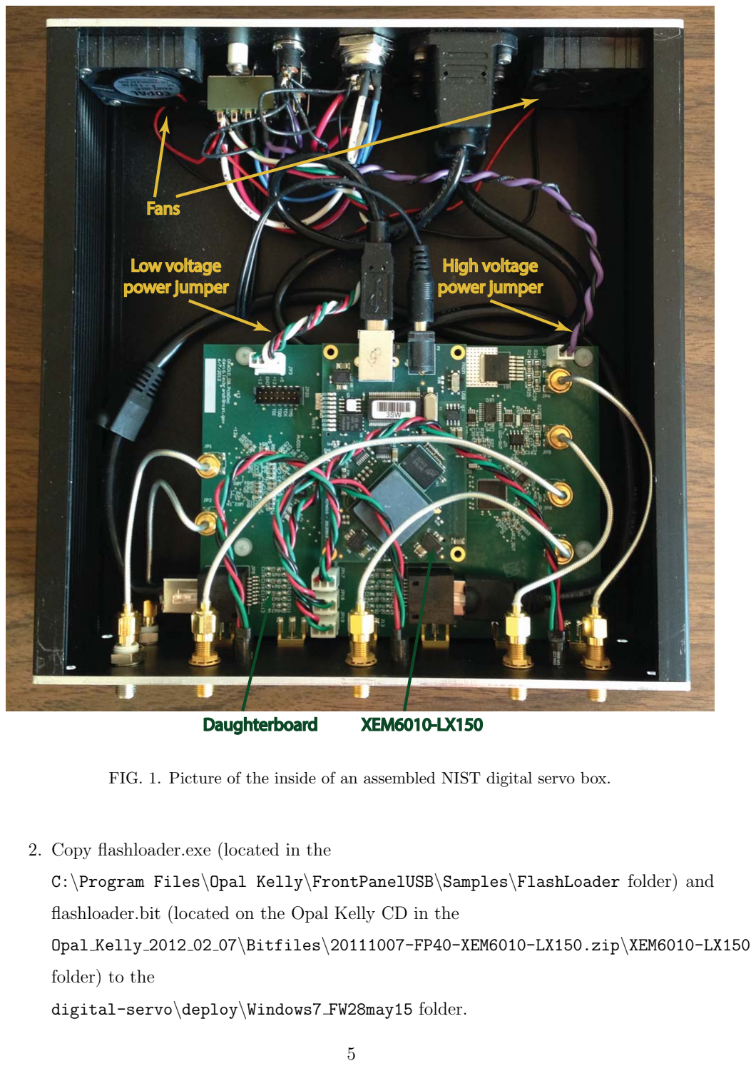
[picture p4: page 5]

Fans

Low voltage Low voltage
power jumper power jumper

High voltage High voltage
power jumper power jumper

Daughterboard Daughterboard XEM6010-LX150 XEM6010-LX150

FIG. 1. Picture of the inside of an assembled NIST digital servo box.

2. Copy flashloader.exe (located in the

C:\Program Files\Opal Kelly\FrontPanelUSB\Samples\FlashLoader folder) and

flashloader.bit (located on the Opal Kelly CD in the

Opal Kelly 2012 02 07\Bitfiles\20111007-FP40-XEM6010-LX150.zip\XEM6010-LX150

folder) to the

digital-servo\deploy\Windows7 FW28may15 folder.

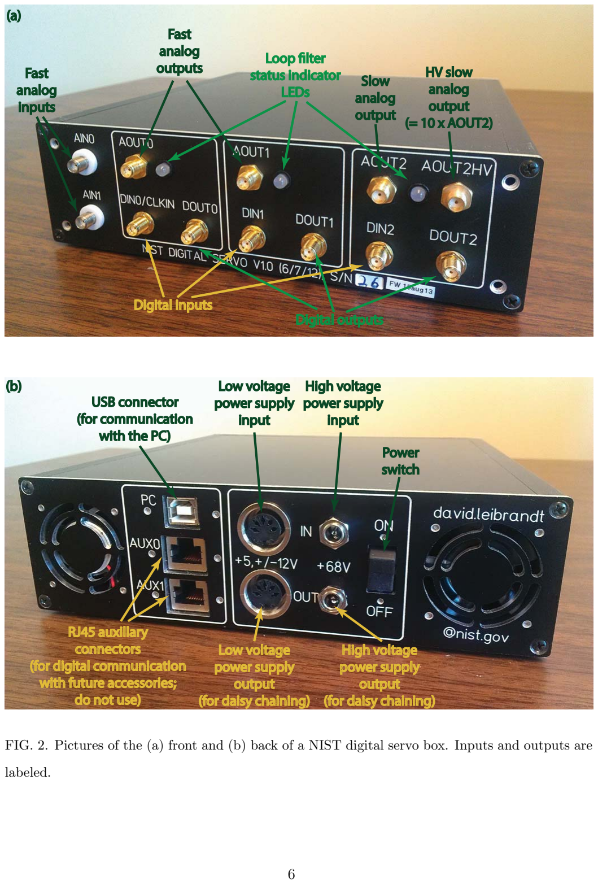
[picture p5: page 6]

Low voltage Low voltage
power supply power supply
input

High voltage High voltage
power supply power supply
input

Low voltage Low voltage
power supply power supply
output
(for daisy chaining) (for daisy chaining)

High voltage High voltage
power supply power supply
output
(for daisy chaining) (for daisy chaining)

Power
switch

USB connector USB connector (for communication (for communication with the PC) with the PC)

RJ45 auxillary RJ45 auxillary
connectors connectors
(for digital communication (for digital communication with future accessories; with future accessories; do not use) do not use)

(b)

(a)

Fast
analog
inputs

Fast
analog
outputs outputs
Slow
analog
output

HV slow HV slow
analog
output
(= 10 x AOUT2) (= 10 x AOUT2)

Digital inputs Digital inputs Digital outputs Digital outputs

Loop filter Loop filter
status indicator status indicator LEDs

FIG. 2. Pictures of the (a) front and (b) back of a NIST digital servo box. Inputs and outputs are

labeled.

3. Unplug all other digital servo boxes from the computer so that flashloader.exe will

select the correct box for for programming.

4. Plug in the digital servo power and USB connections and flip the dip switch on the

XEM6010-LX150 to “USB” (you will have to open the digital servo enclosure), then

flip the power switch to the on position.

5. Open a command prompt (search for “cmd” in the Start Menu) and navigate to the

digital-servo\deploy\Windows7 FW28may15 folder.

6. Execute

flashloader.exe superlaserland HW07jun12 CONFIG SIMPLEPI FW28may15.bit

7. Flip the dip switch on the XEM6010-LX150 to “PROM”, then power cycle the digital

servo and close up the enclosure.

C. Installing the software

Follow these steps to install the GUI:

1. If you have not already done so on this computer, install the Opal Kelly communication

driver (see Section II B, step 1).

2. Copy okFrontPanel.dll (located in the

C:\Program Files\Opal Kelly\FrontPanelUSB\API-32 folder) to the

digital-servo\deploy\Windows7 FW28may15 folder.

3. Create an empty folder C:\data\SuperLaserLand. This is the location where any

data saved by the digital servo can be found.

4. Connect the low voltage and high voltage power supplies. Note that there are two

connectors for each power supply on the back of the digital servo box. This is to

allow running up to four digital servo boxes on a single pair of power supplies, using

daisy chain cables. Also note that if you do not intend to use the high voltage output

(AOUT2HV), you do not need the high voltage power supply.

5. Ensure that the power switch on the back of the digital servo is in the off position,

then connect the USB cable to the back of the digital servo box and to your PC.

6. Flip the power switch on the back of the digital servo to the on position and wait 15 s

for the FPGA to initialize.

7. Run the executable SuperLaserLand FW28may15.exe and you should be ready to go!

See Sec. III for a description of how to use the GUI.

III. GRAPHICAL USER INTERFACE

Communication between the NIST digital servo hardware and the computer is facilitated

by a GUI program called SuperLaserLand (see Fig. 3). Follow the instructions found in

Sec. II C in order to launch SuperLaserLand.

A. Device menu

The Device menu contains commands pertaining to the digital servo hardware. The Set

name command is used to set the name of the digital servo box. This name is displayed

at the top left of the SuperLaserLand window and is helpful when communicating with

multiple digital servo boxes using a single PC. If the GUI is launched when more than one

digital servo box is connected to the computer, the user will be asked to select the hardware

box they wish to communicate with by this name. The Send command, Optimize LTC2195

timing, and Optimize AD9783 timing commands are used for debugging and should not

be needed by the typical user.

B. Config menu

The Config menu contains commands for saving and loading the digital servo configu-

ration (i.e., digital signal processing settings). The current configuration can be saved to or

loaded from a FLASH memory located in the digital servo box using the Save to FLASH

or Load from FLASH commands. The FLASH memory can only hold one configuration at

a time, so any previously saved configuration is overwritten each time the Save to FLASH

command is used. The FLASH memory is nonvolatile, and the configuration saved in the

Fast
analog
input
settings settings

Lockin
amplifier amplifier
settings settings

Phase
detector detector
settings settings

Scope
settings settings

Scope
plot

Lock box Lock box
name

(b)

(a)

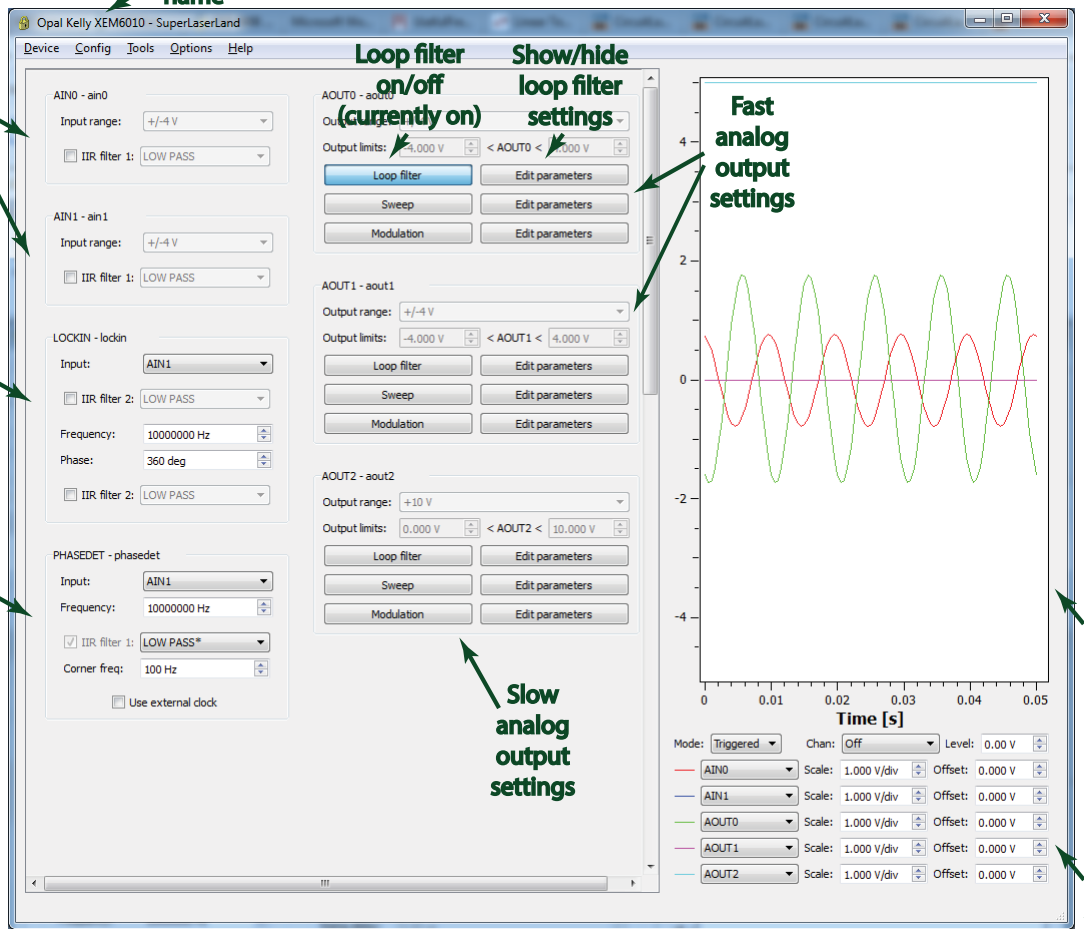
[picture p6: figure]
Fast analog output settings settings; Slow analog output settings settings; Loop filter Loop filter on/off (currently on) (currently on); Show/hide Show/hide loop filter loop filter settings settings

VGA setting VGA setting
Firmware output range limits Firmware output range limits

Loop filter input signal, offset, and sign Loop filter input signal, offset, and sign
Second order IIR filter (currently disabled) Second order IIR filter (currently disabled)

First order IIR filter First order IIR filter
(currently enabled and set to a PI loop shape) (currently enabled and set to a PI loop shape)

First order IIR filter First order IIR filter
(currently enabled and set to a PD loop shape) (currently enabled and set to a PD loop shape)

First order IIR filter (currently disabled) First order IIR filter (currently disabled)
Loop filter hold (currently disabled) Loop filter hold (currently disabled)
Loop filter hold falling and rising edge delay Loop filter hold falling and rising edge delay

Sweep center Sweep center
Sweep amplitude Sweep amplitude
Sweep frequency Sweep frequency

Amplitude of LOCKIN LO added to AOUT0 Amplitude of LOCKIN LO added to AOUT0

LOCKIN LO frequency LOCKIN LO frequency and phase and phase
LOCKIN post-filter LOCKIN post-filter

LOCKIN pre-filter LOCKIN pre-filter

LOCKIN input signal LOCKIN input signal

PHASEDET input signal PHASEDET input signal PHASEDET LO frequency PHASEDET LO frequency PHASEDET post-filter PHASEDET post-filter (currently set to a (currently set to a low-pass with a low-pass with a corner frequency corner frequency of 100 Hz.) of 100 Hz.)

AIN0 post-filter AIN0 post-filter (currently disabled) (currently disabled)

AOUT0 settings: AOUT0 settings: AIN0 VGA setting AIN0 VGA setting

Loop filter automatic relock (currently disabled) Loop filter automatic relock (currently disabled)

Loop filter clear when railed (currently disabled) Loop filter clear when railed (currently disabled)

FIG. 3. Screen shots of the SuperLaserLand GUI. The settings for the AOUT loop filter, sweep,

and modulation can be (a) hidden or (b) shown. Most of the configuration settings are labeled.

FLASH memory is loaded automatically on power up. The current configuration can also

be saved to or loaded from the PC, using the Save to file or Load from file commands.

This allows the user to save multiple configuration files and to transfer the configuration

from one digital servo to another (via the PC).

C. Tools menu

The Tools menu contains commands used for diagnostics of the digital servo and the

system under servo control.

The Record data command is used to record all of the digital servo signals to a bi-

nary file on the PC at a user defined sample rate and for a user defined total number of

samples. The resulting data file can be found in C:\data\SuperLaserLand and is labeled

<TIMESTAMP>.dat. It can be read into matlab using the function

readSuperLaserLandSimplePI.m located in the digital-servo\matlab folder.

The Measure transfer function command is used to measure transfer functions. It

temporarily adds a swept sinusoidal modulation to one of the analog outputs. For each

value of the modulation frequency, a data file containing the values of digital servo sig-

nals is recorded to the PC (by internally calling the Record data command). The data

files can be found in the directory C:\data\SuperLaserLand\<TIMESTAMP> and are la-

beled <MODULATION FREQ>.dat. Data processing to compute the transfer function from

the recorded files is performed offline in matlab.

D. Options menu

The Options menu contains software options.

The Edit analog configuration option must be enabled in order to be able to change

the analog input and output ranges. This prevents the user from accidentally changing the

input and output ranges, which in some circumstances may damage the system under servo

control. In addition, when the Edit analog configuration option is enabled, the user

can change the names of the analog signals by typing a new name in the Name text field

that appears at the top of the signal box and pressing enter. For instance, AIN0 could be

renamed “HC error signal” and AOUT2 could be named “PZT”. These names are saved with the digital servo configuration.

When the Log data option is enabled, the digital servo records the values of the analog

signals to a text file on the PC at a user defined interval, indefinitely. At the end of

each time interval the minimum, maximum, and mean values of each signal over the time

interval are recorded. The data file can be found in C:\data\SuperLaserLand and is labeled

<TIMESTAMP>.csv. It can be read into matlab using the function readSLLlog.m located in

the digital-servo\matlab folder.

E. Analog input configuration

Each analog input has configuration settings located in the AIN0 and AIN1 boxes that

allow processing of the input signals before they are used for feedback. The gain of the VGA

before the ADC can be set using the Input range drop down list, which can only be accessed

when the Edit analog configuration option is enabled. In addition, the digitized ADC

signal can optionally be filtered by a first order IIR filter. In order to enable the IIR filter,

click the checkbox to the left of the label IIR filter 1 (which stands for first order IIR

filter). The filter shape can be changed using the drop down list, and the filter parameters

can be set using the numerical input boxes below. For example, when the filter shape is set

to LOW PASS, the low-pass corner frequency and gain can be adjusted.

F. Lock-in amplifier configuration

The lock-in amplifier settings are located in the box labeled LOCKIN. From top to bottom

the settings are the input signal (Input drop down list), the second order IIR pre-filter

(top IIR filter 2), the LO frequency and demodulation phase, and the second order IIR

post-filter (bottom IIR filter 2).

G. Phase detector configuration

The phase detector settings are located in the box labeled PHASEDET. From top to bottom

the settings are the input signal (Input drop down list), the LO frequency, the first order

low-pass IIR filter frequency, and the use external clock setting. Note that that majority

of the FPGA is clocked on an internal crystal oscillator clock, and that the phase detector optionally uses an external clock to clock the local oscillator. The external clock must be

a square wave fed into DIN0, have a low level of 0 V and a high level of 3.3 V, and have a

frequency of 10 MHz.

H. Analog output configuration

The analog output settings are located in the AOUT0, AOUT1, and AOUT2 boxes. The gain of

the VGA after the DAC can be set using the Output range drop down list and the firmware

output range limits can be set using the Output limits numerical input boxes. These

settings can only be accessed when the Edit analog configuration option is enabled.

Each analog output signal is generated as the sum of a loop filter, a sweep module

that generates a triangle wave sweep, and a relock module that performs automatic lock

acquisition.

The analog output loop filter can be turned on or off using the Loop filter button.

When SuperLaserLand is first opened, the loop filter settings are hidden. In order to display

the loop filter settings, press the Edit parameters button to the right of the Loop filter

button. The loop filter input can be set to any of the analog signals with an optional constant

offset and sign flip. The loop filter consists of one or more first and second order IIR filters

applied sequentially to the input signal. The settings for these filters are shown from top

to bottom in the order the filters are applied, starting with a second order IIR filter (IIR

filter 2) and followed by one to three first order IIR filters (IIR filter 1). Only the

first first-order IIR filter must be enabled; the other IIR filters are optional. For example, a

“PIID” loop shape can be configured by disabling the second order IIR filter and enabling

the three first order IIR filters, with loop shapes PI, PI, and PD. Alternatively, an integrator

with a notch (appropriate for feedback to a PZT with a resonance) can be configured by

enabling the second order IIR filter and the first first-order IIR filter with loop shapes I/HO

and P (note that I/HO stands for integrator divided by harmonic oscillator). Note that

the first and second order IIR filters have latencies of 30 and 80 ns. The latency of each

module should be kept in mind when selecting a loop filter configuration for high-bandwidth

applications.

An optional loop filter hold feature (“integrator hold”) can be enabled using the checkbox

to the left of the label Hold. When this feature is enabled, the output of the loop filter will be constant when the signal selected to the right of the label Hold is boolean true. When

DIN0, DIN1, or DIN2 is selected, the loop filter output is held constant when the digital

input is TTL high. When !DIN0, !DIN1, or !DIN2 is selected, the loop filter output is held

constant when the digital input is TTL low. When LOOP FILTER 0, 1, or 2 is selected, the

loop filter output is held constant when the other loop filter is unlocked (which is detected

only if the relock feature on that loop filter is enabled). The falling and rising edges of the

hold signal can optionally be delayed by independent time intervals, which are set using the

Falling delay and Rising delay input boxes. This feature is useful, for instance, when

performing intensity stabilization of a short laser pulse.

An optional loop filter automatic relock feature can be enabled using the checkbox to

the left of the label Relock. To the right of the Relock label there is a drop down list that

allows the user to select the signal that will determine whether the loop filter is locked or

not. When an analog signal is selected, the loop filter is considered locked when the value

of that analog signal is between the user input bounds. When a digital signal is selected,

the loop filter is considered locked when the digital signal is TTL low. When the loop filter

is unlocked, the relock feature sweeps the output of the loop filter in a triangle wave with

an amplitude that increases with time and a (constant) user selected slew rate, until lock is

reacquired.

Finally, the loop filter output can optionally be reset to zero when it reaches one of the

output limits using the checkbox to the left of the label Clear integrators when railed.

This feature is useful for locking cavities or interferometers where the error signal is periodic

and it does not matter to which fringe the system is locked.

The analog output sweep can be turned on or off using the Sweep button, and the sweep

settings can be shown by pressing the Edit parameters button to the right of the Sweep

button. The sweep is a triangle wave, with adjustable offset (Center input box), amplitude,

and frequency. In order to DC bias the analog output, turn on the sweep with zero amplitude.

The lock-in amplifier LO can be added to the analog output by pressing the Modulation

button, and the modulation amplitude can be shown and adjusted by pressing the Edit

parameters button to the right of the Modulation button.

I. Scope configuration

The right side of the SuperLaserLand GUI contains a basic oscilloscope that can be used

to display the digital servo signals in real-time. The oscilloscope has three modes: Off,

Rolling, and Triggered. When Rolling mode is selected the time base of the scope is 20 s,

and when Triggered mode is selected the time base of the scope is 50 ms. These are not

adjustable. The oscilloscope can display up to five traces simultaneously. For each trace,

the user can select the digital servo signal to be displayed, the vertical scale, and the vertical

offset.

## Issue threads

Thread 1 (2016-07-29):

### ISSUE TITLE
no NC format drill file

### ISSUE THREAD

**Issue by aaronvt** [nist-ionstorage/digital-servo#1]
I dont have altium, but would like to make a few copies from somewhere like OSHPark.com.  It reads al the gerbers correctly, but says there is no drills, it needs them in NC format not the altium GG1 DD1 , would it be possible to add a compatible NC drill file?

http://support.oshpark.com/support/solutions/articles/136065-altium-drill-files

**Comment by dleibrandt** [comment]
Sure thing.  I think I've gotten all the settings correct now.  See:
/hardware/Project Outputs for OK6010_DB/OK6010_DB.TXT

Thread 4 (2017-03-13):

### ISSUE TITLE
Matlab script for measuring transfer function 

### ISSUE THREAD

**Issue by daiweizhu** [nist-ionstorage/digital-servo#4]
@dleibrandt  Can you share a sample script for calculating the transfer function from the files generated by the "measure transfer function" tool in GUI? I was able to read in single files in Matlab with the readSuperLaserLandSimplePI. But I don't know how to combine all the files.
Thanks a lot!

**Comment by dleibrandt** [comment]
See https://github.com/nist-ionstorage/digital-servo/blob/master/matlab/plotTransferFunction.m.

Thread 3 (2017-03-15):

### ISSUE TITLE
testing RJ45 and digital connectors

### ISSUE THREAD

**Issue by jbqubit** [nist-ionstorage/digital-servo#3]
@dleibrandt Does GUI include provision to test connectivity of RJ45 an digital IO connectors? technosystem would like to make simple test to validate assembled units.

**Comment by dleibrandt** [comment]
RJ45 - Not presently, although it wouldn't be too difficult to put something in.  Did you have anything in particular in mind?

Digital IO - Yes, but not in the standard version of the firmware.  For testing, I use a different firmware, which I just uploaded to [here](https://github.com/nist-ionstorage/digital-servo/blob/master/deploy/Windows7_FW28may15/superlaserland_HW07jun12_CONFIG_TESTHARDWARE_FW20mar15.bit).  In it, there is no GUI settable configuration.  Instead, the outputs mirror the inputs as follows:

AOUT0,1 and AIN0,1 are set to +/- 4 V range 
AOUT0 = AIN0 
AOUT1 = AIN1 
AOUT2 = AIN1 
DOUTx = DINx 
LEDs = orange

**Comment by jbqubit** [comment]
> Digital IO - Yes, but not in the standard version of the firmware.
> outputs mirror the inputs

Perfect. That's a good test. And nice that it doesn't require interaction
with the GUI.

For testing RJ45, a simple functionality test is AUX1 output mirroring AUX0
input. If you have bandwidth please generate a firmware that adds this
test. This will put technosystem in a good position to build and test boxes
for many groups. :)

-Joe




Joe Britton
Sensors and Electron Devices
Army Research Lab
2800 Powder Mill Rd
Adelphi, MD 20783
301-394-3130
joseph.w.britton5.civ@mail.mil

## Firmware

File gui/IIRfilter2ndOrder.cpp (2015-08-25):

#include <QHBoxLayout>
#include <QVBoxLayout>

#include "LockBox.h"
#include "IIRfilter2ndOrder.h"
#include "common.h"

IIRfilter2ndOrder::IIRfilter2ndOrder(LockBox *parent, unsigned int configOffset, int a0shift, int updateEvery, bool alwaysOn, QStringList *filterTypes, int labelSize, int widgetSize) :
  QWidget(0),
  parent(parent),
  configOffset(configOffset),
  updateEvery(updateEvery),
  alwaysOn(alwaysOn),
  SETTING_WIDGETS_FROM_CONFIG(false),
  SETTING_WIDGETS_VISIBLE(false),
  SETTING_COEFFICIENTS_FROM_PARAMETERS(false),
  SETTING_PARAMETERS_FROM_COEFFICIENTS(false)
{
  QVBoxLayout *mainLayout = new QVBoxLayout(this);

  a0 = 0x1LL << a0shift;

  // Filter on/off and type
  {
    QHBoxLayout *hLayout = new QHBoxLayout();
    FilterOnCheckBox = new QCheckBox(tr("IIR filter 2:"));
    FilterTypeComboBox = new QComboBox();

    FilterOnCheckBox->setMinimumSize(labelSize, 0);
    FilterOnCheckBox->setSizePolicy(QSizePolicy::Fixed, QSizePolicy::Fixed);
    if (alwaysOn)
    {
      FilterOnCheckBox->setChecked(true);
      FilterOnCheckBox->setEnabled(false);
    }

    for (int i = 0; i < filterTypes->length(); i ++)
    {
      FilterTypeComboBox->addItem(filterTypes->value(i));
    }

    FilterTypeComboBox->setMinimumSize(widgetSize, 0);
    FilterTypeComboBox->setSizePolicy(QSizePolicy::Fixed, QSizePolicy::Fixed);

    hLayout->addWidget(FilterOnCheckBox);
    hLayout->addWidget(FilterTypeComboBox);
    mainLayout->addLayout(hLayout);
  }

  // Corner frequency spin box
  {
    QHBoxLayout *hLayout = new QHBoxLayout();
    freqLabel = new QLabel(tr("Corner freq:"));
    freqSpinBox = new VariableDoubleSpinBox();

    freqLabel->setMinimumSize(labelSize, 0);
    freqLabel->setSizePolicy(QSizePolicy::Fixed, QSizePolicy::Fixed);

    freqSpinBox->setSuffix(tr(" Hz"));
    freqSpinBox->setDecimals(0);
    freqSpinBox->setSingleStep(10);

    freqSpinBox->setMinimumSize(widgetSize, 0);
    freqSpinBox->setSizePolicy(QSizePolicy::Fixed, QSizePolicy::Fixed);

    hLayout->addWidget(freqLabel);
    hLayout->addWidget(freqSpinBox);
    mainLayout->addLayout(hLayout);
  }

  // Q
  {
    QHBoxLayout *hLayout = new QHBoxLayout();
    qualityFactorLabel = new QLabel(tr("Q:"));
    qualityFactorSpinBox = new VariableDoubleSpinBox();

    qualityFactorLabel->setMinimumSize(labelSize, 0);
    qualityFactorLabel->setSizePolicy(QSizePolicy::Fixed, QSizePolicy::Fixed);

    qualityFactorSpinBox->setDecimals(2);
    qualityFactorSpinBox->setSingleStep(1);

    hLayout->addWidget(qualityFactorLabel);
    hLayout->addWidget(qualityFactorSpinBox);
    mainLayout->addLayout(hLayout);
  }

  // Gain
  {
    QHBoxLayout *hLayout = new QHBoxLayout();
    gainLabel = new QLabel(tr("Gain:"));
    gainSpinBox = new VariableDoubleSpinBox();

    gainLabel->setMinimumSize(labelSize, 0);
    gainLabel->setSizePolicy(QSizePolicy::Fixed, QSizePolicy::Fixed);

    gainSpinBox->setSuffix(tr(" dB"));
    gainSpinBox->setDecimals(1);
    gainSpinBox->setSingleStep(1);

    hLayout->addWidget(gainLabel);
    hLayout->addWidget(gainSpinBox);
    mainLayout->addLayout(hLayout);
  }

  // Gain limit
  {
    QHBoxLayout *hLayout = new QHBoxLayout();
    gainLimitLabel = new QLabel(tr("Gain limit:"));
    gainLimitSpinBox = new VariableDoubleSpinBox();

    gainLimitLabel->setMinimumSize(labelSize, 0);
    gainLimitLabel->setSizePolicy(QSizePolicy::Fixed, QSizePolicy::Fixed);

    gainLimitSpinBox->setSuffix(tr(" dB"));
    gainLimitSpinBox->setDecimals(0);
    gainLimitSpinBox->setSingleStep(5);

    hLayout->addWidget(gainLimitLabel);
    hLayout->addWidget(gainLimitSpinBox);
    mainLayout->addLayout(hLayout);
  }

  // a0 spin box
  {
    QHBoxLayout *hLayout = new QHBoxLayout();
    a0Label = new QLabel(tr("a0:"));
    a0SpinBox = new QLabel("2<sup>" + locale().toString(a0shift) + "</sup>");

    a0Label->setMinimumSize(labelSize, 0);
    a0Label->setSizePolicy(QSizePolicy::Fixed, QSizePolicy::Fixed);

    a0SpinBox->setMinimumSize(widgetSize, 0);
    a0SpinBox->setSizePolicy(QSizePolicy::Fixed, QSizePolicy::Fixed);

    hLayout->addWidget(a0Label);
    hLayout->addWidget(a0SpinBox);
    mainLayout->addLayout(hLayout);
  }

  // a1 spin box
  {
    QHBoxLayout *hLayout = new QHBoxLayout();
    a1Label = new QLabel(tr("a1:"));
    a1SpinBox = new VariableLongLongSpinBox();

    a1Label->setMinimumSize(labelSize, 0);
    a1Label->setSizePolicy(QSizePolicy::Fixed, QSizePolicy::Fixed);

    a1SpinBox->setRange(-17179869184, 17179869183);
    a1SpinBox->setSingleStep(1);
    a1SpinBox->setValue(0);

    a1SpinBox->setMinimumSize(widgetSize, 0);
    a1SpinBox->setSizePolicy(QSizePolicy::Fixed, QSizePolicy::Fixed);

    hLayout->addWidget(a1Label);
    hLayout->addWidget(a1SpinBox);
    mainLayout->addLayout(hLayout);
  }

  // a2 spin box
  {
    QHBoxLayout *hLayout = new QHBoxLayout();
    a2Label = new QLabel(tr("a2:"));
    a2SpinBox = new VariableLongLongSpinBox();

    a2Label->setMinimumSize(labelSize, 0);
    a2Label->setSizePolicy(QSizePolicy::Fixed, QSizePolicy::Fixed);

    a2SpinBox->setRange(-17179869184, 17179869183);
    a2SpinBox->setSingleStep(1);
    a2SpinBox->setValue(0);

    a2SpinBox->setMinimumSize(widgetSize, 0);
    a2SpinBox->setSizePolicy(QSizePolicy::Fixed, QSizePolicy::Fixed);

    hLayout->addWidget(a2Label);
    hLayout->addWidget(a2SpinBox);
    mainLayout->addLayout(hLayout);
  }

  // b0 spin box
  {
    QHBoxLayout *hLayout = new QHBoxLayout();
    b0Label = new QLabel(tr("b0:"));
    b0SpinBox = new VariableLongLongSpinBox();

    b0Label->setMinimumSize(labelSize, 0);
    b0Label->setSizePolicy(QSizePolicy::Fixed, QSizePolicy::Fixed);

    b0SpinBox->setRange(-17179869184, 17179869183);
    b0SpinBox->setSingleStep(1);
    b0SpinBox->setValue(0);

    b0SpinBox->setMinimumSize(widgetSize, 0);
    b0SpinBox->setSizePolicy(QSizePolicy::Fixed, QSizePolicy::Fixed);

    hLayout->addWidget(b0Label);
    hLayout->addWidget(b0SpinBox);
    mainLayout->addLayout(hLayout);
  }

  // b1 spin box
  {
    QHBoxLayout *hLayout = new QHBoxLayout();
    b1Label = new QLabel(tr("b1:"));
    b1SpinBox = new VariableLongLongSpinBox();

    b1Label->setMinimumSize(labelSize, 0);
    b1Label->setSizePolicy(QSizePolicy::Fixed, QSizePolicy::Fixed);

    b1SpinBox->setRange(-17179869184, 17179869183);
    b1SpinBox->setSingleStep(1);
    b1SpinBox->setValue(0);

    b1SpinBox->setMinimumSize(widgetSize, 0);
    b1SpinBox->setSizePolicy(QSizePolicy::Fixed, QSizePolicy::Fixed);

    hLayout->addWidget(b1Label);
    hLayout->addWidget(b1SpinBox);
    mainLayout->addLayout(hLayout);
  }

  // b2 spin box
  {
    QHBoxLayout *hLayout = new QHBoxLayout();
    b2Label = new QLabel(tr("b2:"));
    b2SpinBox = new VariableLongLongSpinBox();

    b2Label->setMinimumSize(labelSize, 0);
    b2Label->setSizePolicy(QSizePolicy::Fixed, QSizePolicy::Fixed);

    b2SpinBox->setRange(-17179869184, 17179869183);
    b2SpinBox->setSingleStep(1);
    b2SpinBox->setValue(0);

    b2SpinBox->setMinimumSize(widgetSize, 0);
    b2SpinBox->setSizePolicy(QSizePolicy::Fixed, QSizePolicy::Fixed);

    hLayout->addWidget(b2Label);
    hLayout->addWidget(b2SpinBox);
    mainLayout->addLayout(hLayout);
  }

  // Hook up on_FilterTypeChanged
  QObject::connect(FilterOnCheckBox, SIGNAL(toggled(bool)), this, SLOT(on_FilterTypeChanged()));
  QObject::connect(FilterTypeComboBox, SIGNAL(currentIndexChanged(int)), this, SLOT(on_FilterTypeChanged()));

  // Hook up on_FilterParametersChanged
  QObject::connect(freqSpinBox, SIGNAL(valueChanged(double)), this, SLOT(on_FilterParametersChanged()));
  QObject::connect(qualityFactorSpinBox, SIGNAL(valueChanged(double)), this, SLOT(on_FilterParametersChanged()));
  QObject::connect(gainSpinBox, SIGNAL(valueChanged(double)), this, SLOT(on_FilterParametersChanged()));
  QObject::connect(gainLimitSpinBox, SIGNAL(valueChanged(double)), this, SLOT(on_FilterParametersChanged()));

  // Hook up on_CoefficientsChanged
  QObject::connect(a1SpinBox, SIGNAL(valueChanged(qint64)), this, SLOT(on_CoefficientsChanged()));
  QObject::connect(a2SpinBox, SIGNAL(valueChanged(qint64)), this, SLOT(on_CoefficientsChanged()));
  QObject::connect(b0SpinBox, SIGNAL(valueChanged(qint64)), this, SLOT(on_CoefficientsChanged()));
  QObject::connect(b1SpinBox, SIGNAL(valueChanged(qint64)), this, SLOT(on_CoefficientsChanged()));
  QObject::connect(b2SpinBox, SIGNAL(valueChanged(qint64)), this, SLOT(on_CoefficientsChanged()));
}

void IIRfilter2ndOrder::set_widgets_from_config()
{
  SETTING_WIDGETS_FROM_CONFIG = true;

  // On/off and type
  if (alwaysOn)
    parent->set_config(configOffset, 0, 0, true);
  else
    FilterOnCheckBox->setChecked(parent->config(configOffset, 0, 0));
  FilterTypeComboBox->setCurrentIndex(parent->config(configOffset, 3, 1));
  set_widgets_visible();

  // IIR coefficients
  a1SpinBox->setValue(parent->config(configOffset + 1, 34, 0, 1));
  a2SpinBox->setValue(parent->config(configOffset + 4, 34, 0, 1));
  b0SpinBox->setValue(parent->config(configOffset + 7, 34, 0, 1));
  b1SpinBox->setValue(parent->config(configOffset + 10, 34, 0, 1));
  b2SpinBox->setValue(parent->config(configOffset + 13, 34, 0, 1));

  // Filter parameters
  if (!(FilterTypeComboBox->currentText() == "CUSTOM"))
    set_parameters_from_coefficients();

  SETTING_WIDGETS_FROM_CONFIG = false;
}

void IIRfilter2ndOrder::on_FilterTypeChanged()
{
  if (SETTING_WIDGETS_FROM_CONFIG || SETTING_WIDGETS_VISIBLE)
    return;

  // On/off and type
  parent->set_config(configOffset, 0, 0, FilterOnCheckBox->isChecked());
  parent->set_config(configOffset, 3, 1, FilterTypeComboBox->currentIndex());
  set_widgets_visible();

  if (!(FilterTypeComboBox->currentText() == "CUSTOM"))
    set_coefficients_from_parameters();
  set_config_from_coefficients();
  if (!(FilterTypeComboBox->currentText() == "CUSTOM"))
    set_parameters_from_coefficients();
}

void IIRfilter2ndOrder::set_config_from_coefficients()
{
  parent->set_config(configOffset, 0, 0, false);

  parent->set_config(configOffset + 1, 34, 0, a1SpinBox->value());
  parent->set_config(configOffset + 4, 34, 0, a2SpinBox->value());
  parent->set_config(configOffset + 7, 34, 0, b0SpinBox->value());
  parent->set_config(configOffset + 10, 34, 0, b1SpinBox->value());
  parent->set_config(configOffset + 13, 34, 0, b2SpinBox->value());

  parent->set_config(configOffset, 0, 0, FilterOnCheckBox->isChecked());
}

void IIRfilter2ndOrder::on_FilterParametersChanged()
{
  if (SETTING_WIDGETS_FROM_CONFIG || SETTING_WIDGETS_VISIBLE || SETTING_PARAMETERS_FROM_COEFFICIENTS)
    return;

  // IIR coefficients
  set_coefficients_from_parameters();
  set_config_from_coefficients();
  set_parameters_from_coefficients();
}

void IIRfilter2ndOrder::on_CoefficientsChanged()
{
  if (SETTING_WIDGETS_FROM_CONFIG || SETTING_WIDGETS_VISIBLE || SETTING_COEFFICIENTS_FROM_PARAMETERS)
    return;

  // IIR coefficients
  set_config_from_coefficients();
}
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

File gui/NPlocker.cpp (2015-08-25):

#include <QHBoxLayout>
#include <QVBoxLayout>
#include <QGroupBox>
#include <QLabel>

#include "LockBoxSimplePI.h"
#include "NPlocker.h"
#include "NP_adjuster.h"
#include "common.h"

#include <stdexcept>

using namespace std;

NPlocker::NPlocker(LockBoxSimplePI *parent, unsigned int configOffset, QString outputName, QStringList *channelNames, double *p_dataIn, int N_dataIn) :
  QWidget(0),
  parent(parent),
  configOffset(configOffset),
  p_dataIn(p_dataIn),
  N_dataIn(N_dataIn),
  Tmin(50),
  Tmax(60),
  SETTING_WIDGETS_FROM_CONFIG(false),
  adjNP(0)
{
  // Make the widget
  int labelSize = 70;
  int widgetSize = 230;

  QGroupBox *mainGroupBox = new QGroupBox(outputName);
  {
    QVBoxLayout *layout = new QVBoxLayout(this);
    layout->addWidget(mainGroupBox);
  }

  QVBoxLayout *mainLayout = new QVBoxLayout();
  mainGroupBox->setLayout(mainLayout);

  // Port
  {
    QHBoxLayout *hLayout = new QHBoxLayout();
	QLabel *label = new QLabel(tr("Port: COM"));
    PortSpinBox = new QSpinBox();

    label->setMinimumSize(labelSize, 0);
    label->setSizePolicy(QSizePolicy::Fixed, QSizePolicy::Fixed);

    PortSpinBox->setRange(0, 99);
	PortSpinBox->setValue(99);
    // QObject::connect(Port, SIGNAL(valueChanged(double)), this, SLOT(setLaserTemp(double)));

    hLayout->addWidget(label);
    hLayout->addWidget(PortSpinBox);
    mainLayout->addLayout(hLayout);
  }

	// Input name
	{
		QHBoxLayout *hLayout = new QHBoxLayout();
		QLabel *label = new QLabel(tr("Command:"));
		CommandLineEdit = new QLineEdit();

		label->setMinimumSize(labelSize, 0);
		label->setSizePolicy(QSizePolicy::Fixed, QSizePolicy::Fixed);

		CommandLineEdit->setMaxLength(16);
		CommandLineEdit->setMinimumSize(widgetSize, 0);
		CommandLineEdit->setSizePolicy(QSizePolicy::Fixed, QSizePolicy::Fixed);

		hLayout->addWidget(label);
		hLayout->addWidget(CommandLineEdit);
		mainLayout->addLayout(hLayout);
	}
  
  // Laser temperature
  {
    QHBoxLayout *hLayout = new QHBoxLayout();
    QLabel *label = new QLabel(tr("Laser temp:"));
    LaserTemp = new QDoubleSpinBox();

    label->setMinimumSize(labelSize, 0);
    label->setSizePolicy(QSizePolicy::Fixed, QSizePolicy::Fixed);

    LaserTemp->setSuffix(tr(" C"));
    LaserTemp->setRange(Tmin, Tmax);
    LaserTemp->setDecimals(3);
    LaserTemp->setSingleStep(0.002);
    QObject::connect(LaserTemp, SIGNAL(valueChanged(double)), this, SLOT(setLaserTemp(double)));

    hLayout->addWidget(label);
    hLayout->addWidget(LaserTemp);
    mainLayout->addLayout(hLayout);
  }

  // Servo on/off
  {
    QHBoxLayout *hLayout = new QHBoxLayout();
    OnOffPushButton = new QPushButton(tr("Servo laser temp"));
    EditPushButton = new QPushButton(tr("Edit parameters"));

    OnOffPushButton->setCheckable(true);

    EditPushButton->setCheckable(true);
    EditPushButton->setChecked(true);

    hLayout->addWidget(OnOffPushButton);
    hLayout->addWidget(EditPushButton);
    mainLayout->addLayout(hLayout);
  }

  // Input
  {
    QHBoxLayout *hLayout = new QHBoxLayout();
    QLabel *label0 = new QLabel(tr("Input:"));
    SignComboBox = new QComboBox();
    QLabel *label1 = new QLabel(tr("("));
    InputComboBox = new QComboBox();
    QLabel *label2 = new QLabel(tr("-"));
    OffsetSpinBox = new QDoubleSpinBox();
    QLabel *label3 = new QLabel(tr(")"));

    label0->setMinimumSize(labelSize, 0);
    label0->setSizePolicy(QSizePolicy::Fixed, QSizePolicy::Fixed);
    label1->setSizePolicy(QSizePolicy::Fixed, QSizePolicy::Fixed);
    label2->setSizePolicy(QSizePolicy::Fixed, QSizePolicy::Fixed);
    label3->setSizePolicy(QSizePolicy::Fixed, QSizePolicy::Fixed);

    SignComboBox->addItem(tr("+"));
    SignComboBox->addItem(tr("-"));
    SignComboBox->setCurrentIndex(1);

    for (int i = 0; i < channelNames->length(); i ++)
    {
      InputComboBox->addItem(channelNames->value(i));
    }
    InputComboBox->setCurrentIndex(6);

    OffsetSpinBox->setSuffix(tr(" V"));
    OffsetSpinBox->setRange(-10, 10);
    OffsetSpinBox->setDecimals(1);
    OffsetSpinBox->setSingleStep(0.1);
    OffsetSpinBox->setValue(5);
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

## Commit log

2015-08-25 initial commit; V1.0
    [Bill of Materials-OK6010_DB.xlsx, Enclosure_BOM.xlsx, OK6010_DB.DRL, OK6010_DB.GBL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]
2016-04-06 added missing matlab file for reading digital servo binary data
2016-07-29 added solder paste to ADC center pad
    [Bill of Materials-OK6010_DB.xlsx, OK6010_DB.DRL, OK6010_DB.GBL, OK6010_DB.GBO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]
2017-01-17 create assembly.md
    Assembly instructions for digital-servo box.
